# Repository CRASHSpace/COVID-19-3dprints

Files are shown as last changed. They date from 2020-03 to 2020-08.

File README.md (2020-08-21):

# COVID-19 3D prints and projects

I. [About us / Our work](#our-work)

II. [Designs](#print-or-laser-cut-ear-savers)

III. [Current needs / print recommendations](#print-recommendation) - Updated 8/21

IV. [Getting parts to us](#drop-off)

*This repo will stay updated with the latest information and source files.*

## Our work

CRASH Space has been working with USC Keck, Cedars-Sinai and others on the front line of this pandemic. With these clinical partners, we have developed and refined designs for face shields, face masks and ear savers, and rallied the community to build them. For the latest information on our work: [https://covid.crashspace.org](https://covid.crashspace.org)

We launched [our GoFundMe](https://charity.gofundme.com/o/en/campaign/makers-united-against-covid-19) on 4/10, and cannot thank our donors enough.

If you'd like to help build or assemble, let us know at covid@crashspace.org or on [this volunteer form](https://docs.google.com/forms/d/e/1FAIpQLSczant_0pGT0tIEJhOTPQsQpFoTAtQAkubEGK8ArdoSDPgAVQ/viewform).

### Drop off
We are collecting donations and assembling kits at: 6323 W 80th St, Los Angeles, CA 90045. Times will be posted on [our calendar](https://calendar.google.com/calendar/embed?src=crashspacela@gmail.com&ctz=America/Los_Angeles).

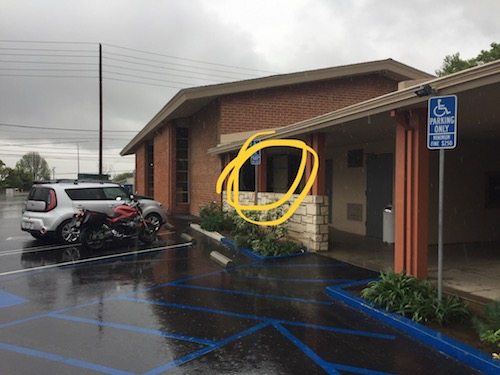
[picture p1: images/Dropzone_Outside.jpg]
Dropzone outside


No contact drop-off area:

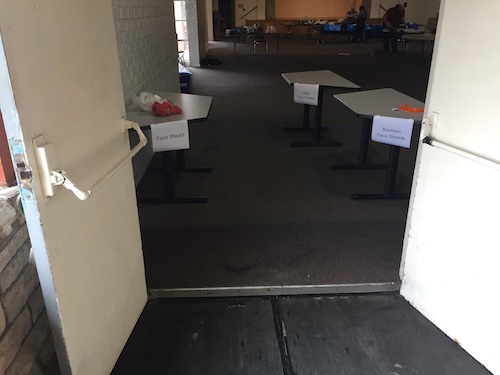
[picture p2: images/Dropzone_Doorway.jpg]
Dropzone doorway drop


**IF YOU MAKE SOMETHING**, please let us know here (We love pictures!): [https://airtable.com/shrZCoERKFkLPPHIm](https://airtable.com/shrZCoERKFkLPPHIm)

**IF YOU'D LIKE A DONATION RECEIPT**, you can get one here: [https://airtable.com/shrjphZT0ER9aLhNy](https://airtable.com/shrjphZT0ER9aLhNy)

## Print recommendation:

**As of late July**, demand for clinical face shields has tapered off as supply chains have caught up. We will announce periodic sprint runs as individual requests come in, and maintain this page for others wanting to produce PPE designs we've validated. As the situation evolves, we too will adapt.

[Sprint Run 8/14 - 8/26: 3DVerkstan Face Shields, V5](#sprint-run-814---826-3dverkstan-face-shields-v5) -- Extended to 8/26

[Sanitation Guidelines](https://github.com/CRASHSpace/COVID-19-3dprints/tree/master/Sanitation%20Guidelines_20200329.pdf)

---

## Sprint Run 8/14 - 8/26: 3DVerkstan Face Shields, V5
[https://github.com/CRASHSpace/COVID-19-3dprints/tree/master/Face%20Shield/3DVerkstan](https://github.com/CRASHSpace/COVID-19-3dprints/tree/master/Face%20Shield/3DVerkstan)

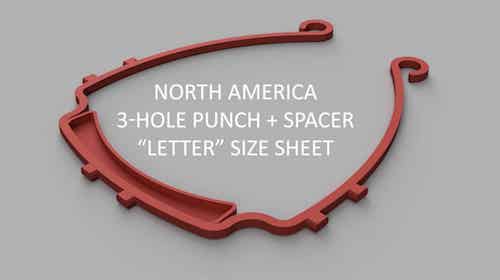
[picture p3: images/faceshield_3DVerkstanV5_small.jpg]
Face shield


LA EOC requested 2000 non-clinical face shields. We can handle making the shields, but need visors printed.

*If you are making some for yourself or another group and need the shield information*: This version uses clear 8.5" x 11" sheets, [3-hole punched to this shape](https://github.com/CRASHSpace/COVID-19-3dprints/raw/master/Face%20Shield/3DVerkstan/Verkstan-3HolePunch-CRASHSpaceMod.pdf). Instructions [here](https://www.youtube.com/watch?v=rz36MhT7p-c&feature=youtu.be). **OR** for large numbers, make [this drill jig from Midsouth Makers](http://www.midsouthmakers.org/2020/04/memphis-fighting-covid-transparency-drilling-rig/#MemphisFightingCOVID)
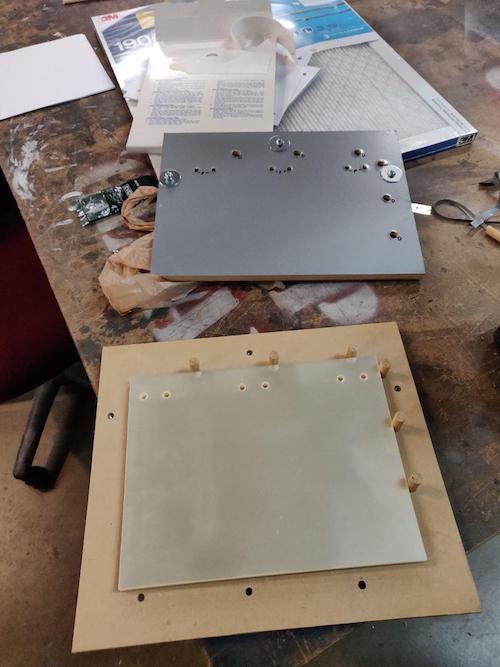
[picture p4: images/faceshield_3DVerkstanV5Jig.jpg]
Verkstan drill jig


## Budmen Face Shields V5 
[https://github.com/CRASHSpace/COVID-19-3dprints/tree/master/Face%20Shield/Budmen%20Face%20Shield/V5](https://github.com/CRASHSpace/COVID-19-3dprints/tree/master/Face%20Shield/Budmen%20Face%20Shield/V5)

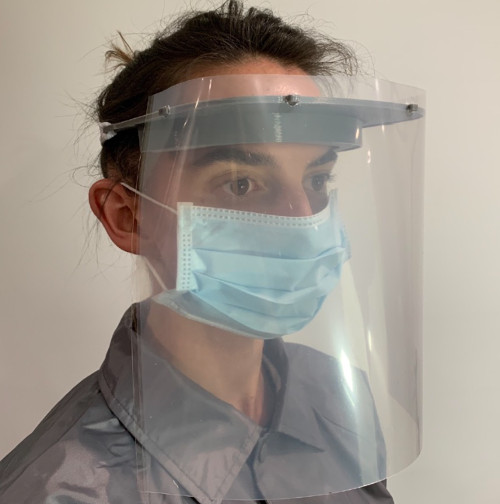
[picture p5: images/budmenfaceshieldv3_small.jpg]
Face shield


Cedars and Keck approved for immediate use. Assembly instructions are [here](https://youtu.be/I1LvKaha7R0). As of 5/25, we are receiving injection molded visors to fill our outstanding requests.

**NOTE:** Our template is different from the stock Budmen shield: [Modified Cedars Budmen shield template](https://github.com/CRASHSpace/COVID-19-3dprints/raw/master/Face%20Shield/Budmen%20Face%20Shield/V3/polysheet-templates/Cedars_Budmen_shield_v1.pdf). Laser template is here: [Cedars_Budmen_shield_v1cut.pdf](https://github.com/CRASHSpace/COVID-19-3dprints/raw/master/Face%20Shield/Budmen%20Face%20Shield/V3/polysheet-templates/Cedars_Budmen_shield_v1cut.pdf)

## Budmen Scrunchie strap
[https://github.com/CRASHSpace/COVID-19-3dprints/tree/master/Face%20Shield/CRASHSpace%20Scrunchy%20Headband](https://github.com/CRASHSpace/COVID-19-3dprints/tree/master/Face%20Shield/CRASHSpace%20Scrunchy%20Headband)

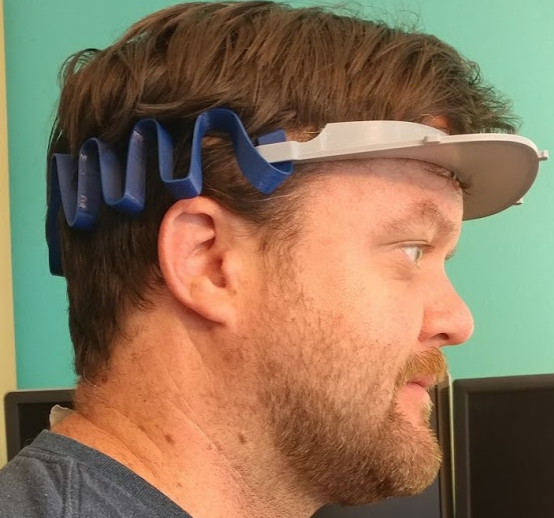
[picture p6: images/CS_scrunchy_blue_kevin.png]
Budmen Scrunchie Strap


Made in response to elastic shortages we faced one month in, these are also more easily sanitized than elastic. Very useful for remote hospitals. PET or PETG only.

## Ear Savers
[https://github.com/CRASHSpace/COVID-19-3dprints/tree/master/Ear%20Savers](https://github.com/CRASHSpace/COVID-19-3dprints/tree/master/Ear%20Savers)

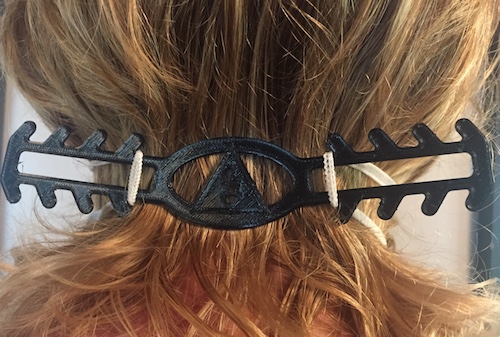
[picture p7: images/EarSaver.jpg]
Ear Saver


Mask bands not tugging on ears == More comfortable. More comfortable == Wear the mask longer (**safer**) + Adjust the mask less (**safer**). If you have a smaller printer, making these is a perfect way to help.

## Fabric Face Masks
[https://github.com/CRASHSpace/COVID-19-3dprints/tree/master/Sewn%20Face%20Mask/COVID_SewnMask-Instructions_v9.pdf](https://github.com/CRASHSpace/COVID-19-3dprints/tree/master/Sewn%20Face%20Mask/COVID_SewnMask-Instructions_v9.pdf)

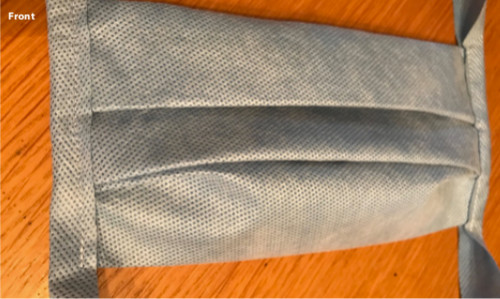
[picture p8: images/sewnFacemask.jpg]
Sewn Face Mask


## USCSW Face Masks
[https://github.com/CRASHSpace/COVID-19-3dprints/tree/master/Face%20Mask](https://github.com/CRASHSpace/COVID-19-3dprints/tree/master/Face%20Mask)

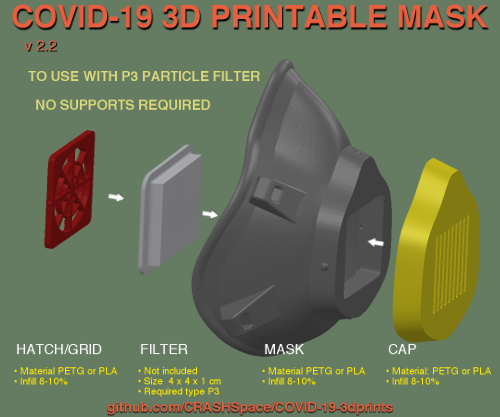
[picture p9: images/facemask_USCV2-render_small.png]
Face Mask Assembly


As of 5/25, we have filled our outstanding requests. We can collect any you have already printed.

## Laser Cut Aerosol Box
[https://github.com/CRASHSpace/COVID-19-3dprints/raw/master/Cedars%20Aerosol%20Box](https://github.com/CRASHSpace/COVID-19-3dprints/raw/master/Cedars%20Aerosol%20Box)

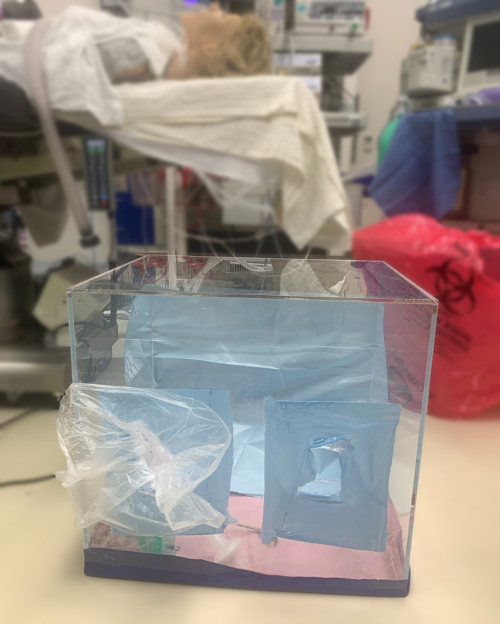
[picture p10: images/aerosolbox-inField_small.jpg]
Cedars Aerosol Box


**Delivered:** 1 evaluation unit for intubation testing

## SMP Face Shield
Just informational. **USC Keck evaluated**, and chose the Budmen design instead.

[https://github.com/CRASHSpace/COVID-19-3dprints/tree/master/Face%20Shield/SMP%20Face%20Shield](https://github.com/CRASHSpace/COVID-19-3dprints/tree/master/Face%20Shield/SMP%20Face%20Shield)

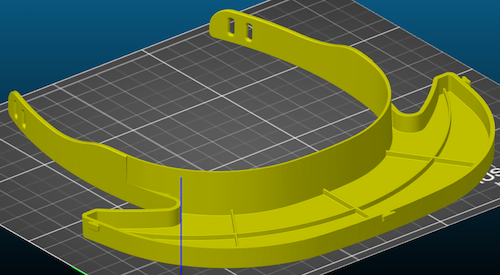
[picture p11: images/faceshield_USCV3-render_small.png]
SMP Face shield


# THANK YOU. Yes, you.

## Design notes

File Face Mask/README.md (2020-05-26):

# Face Masks (USC Keck modified Lowell design)—V3a updated 5/13
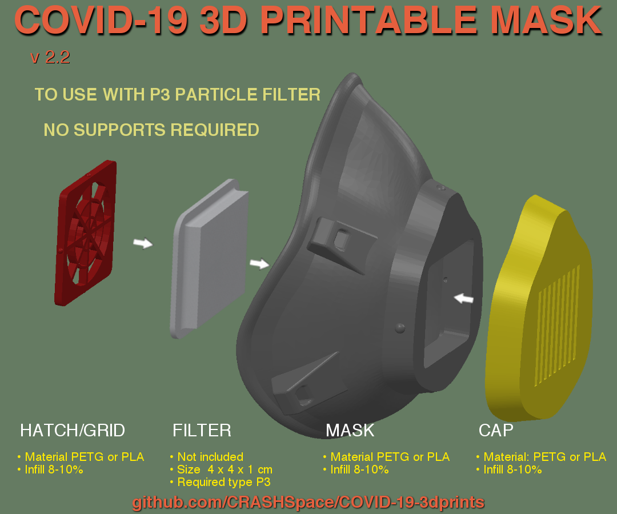
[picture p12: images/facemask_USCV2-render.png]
Face mask render


## Each mask consists of:
**1 x** [USCSW-Filtered_Mask-v3L.stl](https://github.com/CRASHSpace/COVID-19-3dprints/raw/master/Face%20Mask/USCSW-Filtered_Mask-v3L.stl) **OR**

[USCSW-Filtered_Mask-v3M.stl](https://github.com/CRASHSpace/COVID-19-3dprints/raw/master/Face%20Mask/USCSW-Filtered_Mask-v3M.stl) **OR**

[USCSW-Filtered_Mask-v3S.stl](https://github.com/CRASHSpace/COVID-19-3dprints/raw/master/Face%20Mask/USCSW-Filtered_Mask-v3S.stl),

**1 x** [USCSW_Nose_Cap_v3.stl](https://github.com/CRASHSpace/COVID-19-3dprints/raw/master/Face%20Mask/USCSW_Nose_Cap_v3.stl)

*and*

**1 x** [USCSW_Hatch_v2r1.stl](https://github.com/CRASHSpace/COVID-19-3dprints/raw/master/Face%20Mask/USCSW_Hatch_v2r1.stl)

*Above files are from USC Keck* [here](https://drive.google.com/drive/folders/11wPkq75T5fu1r9JX5doEOuPz13cvkt-k). GitHub copies here are intended as backup.

USCSW_gasket_x5S.stl, USCSW_gasket_x5M.stl and USCSW_gasket_x5L.stl are for molding tests. DON'T PRINT

**Print material:** PETG or PLA

**Suggested settings:** *Largest layer size option, up to 0.6mm DRAFT* with *~10% infill*.

## Parts you need to assemble:
DO NOT assemble if delivering to USC Keck. This is for assembling one for yourself.

* [Frost King 5/16" x1/4" D Profile Premium Rubber Self-Stick Weatherseal](https://smile.amazon.com/Frost-King-Self-Stick-Weatherseal-D-Section/dp/B000B4N3O0/ref=sr_1_1?keywords=Frost+King+5%2F16%22+x1%2F4%22+D+Profile+Premium+Rubber+Self-Stick+Weatherseal&qid=1585453260&s=home-garden&sr=1-1). 
* [Honeywell HEPA filter model HRF201B](https://smile.amazon.com/Flintar-Replacement-Compatible-Honeywell-HRF201B/dp/B07SQ5NHJ7/ref=sr_1_5)
* 1/4" or 1/2" Elastic

**[Assembly Guidelines](https://github.com/CRASHSpace/COVID-19-3dprints/blob/master/Face%20Mask/Pseudo%20N95%203D%20Printed%20Masks.pdf)**  

**[Assembly Video - Youtube](https://www.youtube.com/watch?v=TImIaytAqlc&feature=youtu.be)**

## Did you print one?
They would also like to know the following:

Name/Company (opt.)

Date

Qty

Printer type

Print materials

This can be recorded [here](https://airtable.com/shrZCoERKFkLPPHIm), or written and submitted with prints.

### 3/29 Update:
> Heads up. I received a batch with some print issues. Some surface imperfections is fine, but issues with the filter interface is bad. Please check to see if those print areas are free of issues before dropping off. That would be awesome.
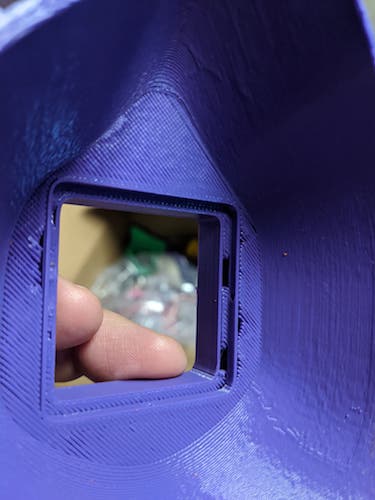
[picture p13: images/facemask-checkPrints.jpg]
Check Prints


### Information:
> We are accepting 3D printed parts. Keck Medical Center will finish attaching padding, filter, and elastic straps. We have two sizes of mask. Currently we are looking to produce a 2:1  M:L. If you are making these for other place or for personal use, we are using [Frost King 5/16" x1/4" D Profile Premium Rubber Self-Stick Weatherseal](https://smile.amazon.com/Frost-King-Self-Stick-Weatherseal-D-Section/dp/B000B4N3O0/ref=sr_1_1?keywords=Frost+King+5%2F16%22+x1%2F4%22+D+Profile+Premium+Rubber+Self-Stick+Weatherseal&qid=1585453260&s=home-garden&sr=1-1). We are sealing around the outer edge with hot glue, but we are experimenting the Flex Seal. The filter is a Honeywell [HEPA filter model HRF201B](https://smile.amazon.com/Flintar-Replacement-Compatible-Honeywell-HRF201B/dp/B07SQ5NHJ7/ref=sr_1_5).
> 
> We are currently printing a variant of the pseudo N95 mask found on [https://lowellmakes.com/covid-19-response/](https://lowellmakes.com/covid-19-response/)
> 
> I’ve included our variants of their model. We are working on more thing including different sizes as well as a process to cast them using resin. I will update people as new models come out.
> 
> We are also working with people to produce face shields. Many of the designs out in the world right now are not wide enough for the liking of our Infection Prevention team. We are laser cutting 13 “ x 9.5” shields and 3D printing head bands. That design is also included (please note the attachment points on the model may need scaling for the thickness of the shield material).
> Any assistance would be most welcomed.
> 
> **Darryl H. Hwang, PhD**
> 
> Assistant Professor of Research, Department of Radiology, Keck School of Medicine
> Assistant Professor of Research, Department of Biomedical Engineering, Viterbi School of Engineering
> Director, 4D Quantitative Imaging Lab, Keck Medical Center of USC

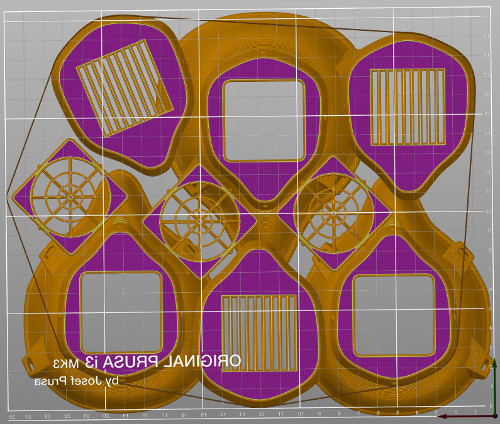
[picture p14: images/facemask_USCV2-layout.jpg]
Face mask layout


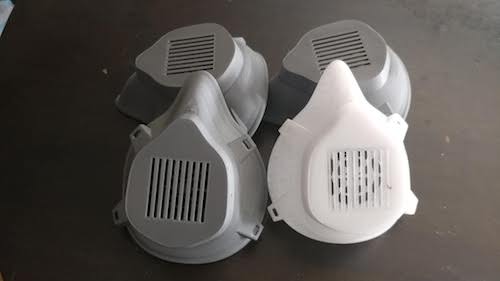
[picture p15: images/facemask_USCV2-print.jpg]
Assembled Face masks


### Source:
Files are **MODIFIED** versions of [Lowell design](https://lowellmakes.com/covid-19-response/)

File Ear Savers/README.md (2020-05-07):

# Ear Savers
Ear Saver

## One part print:
**1 x** [CS CutOut Ear Saver.stl](https://github.com/CRASHSpace/COVID-19-3dprints/raw/master/Ear%20Savers/CS%20CutOut%20Ear%20Saver.stl)

**Print material:** PETG or PLA

## Or Laser Cut:
**Full sheets** 

[EarSaversFullsheet_CS_v2.pdf](https://github.com/CRASHSpace/COVID-19-3dprints/raw/master/Ear%20Savers/EarSaversFullsheet_CS_v2.pdf)

[EarSaversFullsheet_CS_v2.ai](https://github.com/CRASHSpace/COVID-19-3dprints/raw/master/Ear%20Savers/EarSaversFullsheet_CS_v2.ai)

**1 x** [EarSaversSingle_CS.ai](https://github.com/CRASHSpace/COVID-19-3dprints/raw/master/Ear%20Savers/EarSaversSingle_CS.ai)

## Did you print one?
They would also like to know the following:

|||
|--- |--- |
|Name/Company| _(optional)_|
|Date| |
|Quantity| |
|Printer type| |
|Print materials| |

This can be recorded [here](https://airtable.com/shrZCoERKFkLPPHIm), or written and submitted with prints.

### Information on Request:
Multiple hospitals have requested these. It makes wearing a mask all day far more comfortable, since the elastic tugs on these instead of your ears.

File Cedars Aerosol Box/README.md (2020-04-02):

# Aerosol box
Intended use:

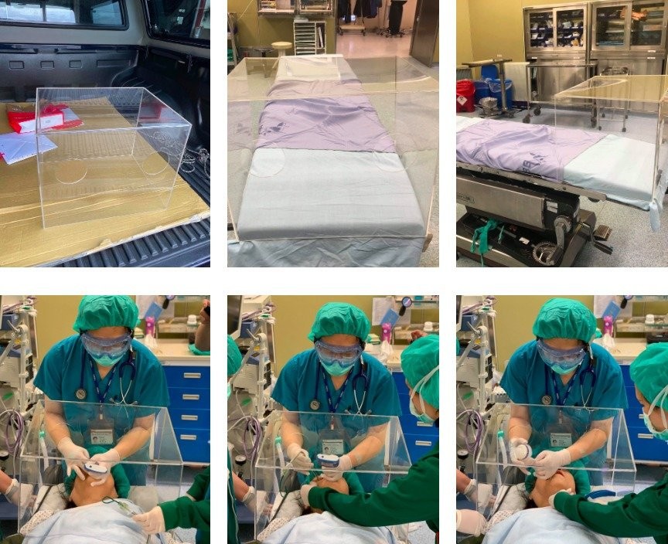
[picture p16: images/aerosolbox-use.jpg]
Intubating patient


## Each unit consists of:
**5 x** Acrylic parts to be cut and plastic welded according to [Aerosol Box.pdf](https://github.com/CRASHSpace/COVID-19-3dprints/raw/master/Cedars%20Aerosol%20Box/Aerosol%20Box.pdf)

## Information on Request:
We delivered a unit to Cedars-Sinai, who requested a unit to evaluate its effectiveness in protecting staff while intubating a patient.

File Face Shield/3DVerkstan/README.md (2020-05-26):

# 3DVerkstan V5 Face Shields
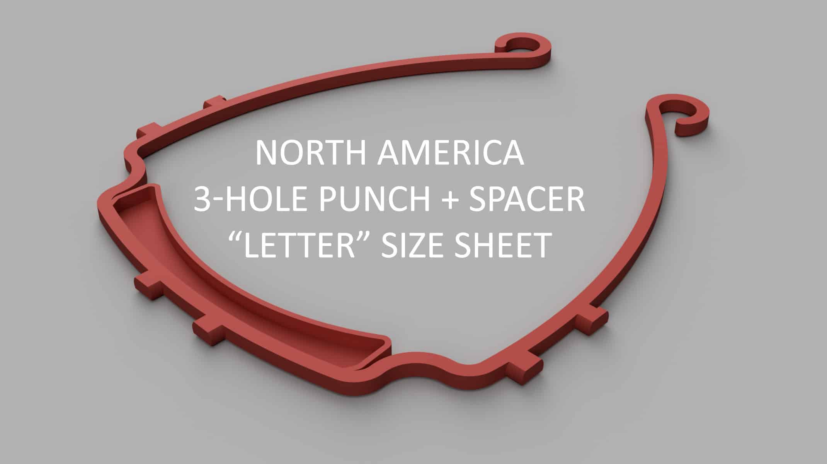
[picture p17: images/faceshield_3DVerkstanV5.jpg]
3DVerkstan Face shield


## Each mask consists of:
**1 x** [Visor_Frame_NORTH_AMERICA_letter_6-hole_v5.stl](https://github.com/CRASHSpace/COVID-19-3dprints/raw/master/Face%20Shield/3DVerkstan/Visor_Frame_NORTH_AMERICA_letter_6-hole_v5.stl)

**1 x** 0.005in thick poly sheet 3-hole punched to guides in [Verkstan-3HolePunch-CRASHSpaceMod.pdf](https://github.com/CRASHSpace/COVID-19-3dprints/raw/master/Face%20Shield/3DVerkstan/Verkstan-3HolePunch-CRASHSpaceMod.pdf)

*and*

**(optional) 1 x** Rubber band

**Print material:** PETG or PLA

**Suggested settings:** *Largest layer size option, up to 0.8mm DRAFT* with *~10% infill*.

### 3DVerkstan Instructions on how to do the punching:

[Video How To](https://www.youtube.com/watch?v=rz36MhT7p-c&feature=youtu.be)

1. Print out the [3 hole punch guide.](https://github.com/CRASHSpace/COVID-19-3dprints/raw/master/Face%20Shield/3DVerkstan/Verkstan-3HolePunch-CRASHSpaceMod.pdf) 100%

2. Tape the guide into your 3-hole punch aligning the first hole to align with the hole punch.

4. To make 12"x11" shields, put the 12" side towards the hole punch. Punch 3 holes

5. Slide the punched plastic sheet to the right, aligning with the guide, and punch 3 more holes.

## Did you print one?
They would also like to know the following:

Name/Company (opt.)

Date

Qty

Printer type

Print materials

This can be recorded [here](https://airtable.com/shrZCoERKFkLPPHIm), or written and submitted with prints.

### Information on Request:
These are being given to non-clinical users.

### Source:
3DVerkstan: [https://3dverkstan.se/protective-visor/protective-visor-versions/](https://3dverkstan.se/protective-visor/protective-visor-versions/)

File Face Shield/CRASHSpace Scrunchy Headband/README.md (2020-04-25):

# CRASHSpace Scrunchy Headband for Budmen Shield
Print!

This is a replacement for the elastic band on the Budmen design. This scrunchy snaps into place and tensions around the user's head to keep the mask firmly in place.

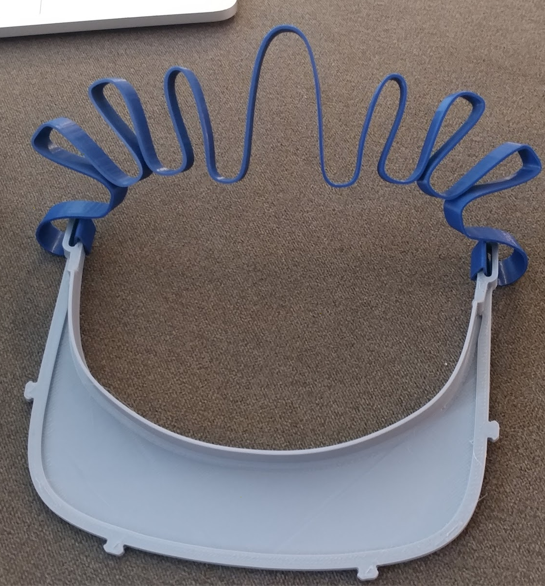
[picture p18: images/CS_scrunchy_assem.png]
CRASHSpace Scrunchy Headband


CRASHSpace Scrunchy Headband

The shortage of elastic is causing us to reconsider how to attach the shields to workers heads. This design requires no elastic and is faster to assemble than with elastic.

Suggest printing in PETG for flexibility.

[CRASHSpace Scrunchy Headband for Budmen Sheild - Large version - STL](https://github.com/CRASHSpace/COVID-19-3dprints/raw/master/Face%20Shield/CRASHSpace%20Scrunchy%20Headband/Crashspace_scrunchy-Budmen-Largev1.STL)

[CRASHSpace Scrunchy Headband for Budmen Sheild - Small version - STL](https://github.com/CRASHSpace/COVID-19-3dprints/raw/master/Face%20Shield/CRASHSpace%20Scrunchy%20Headband/Crashspace_scrunchy-Budmen-Smallv1.STL)

While printing, please set your seam to "Rear" or not on the path. 
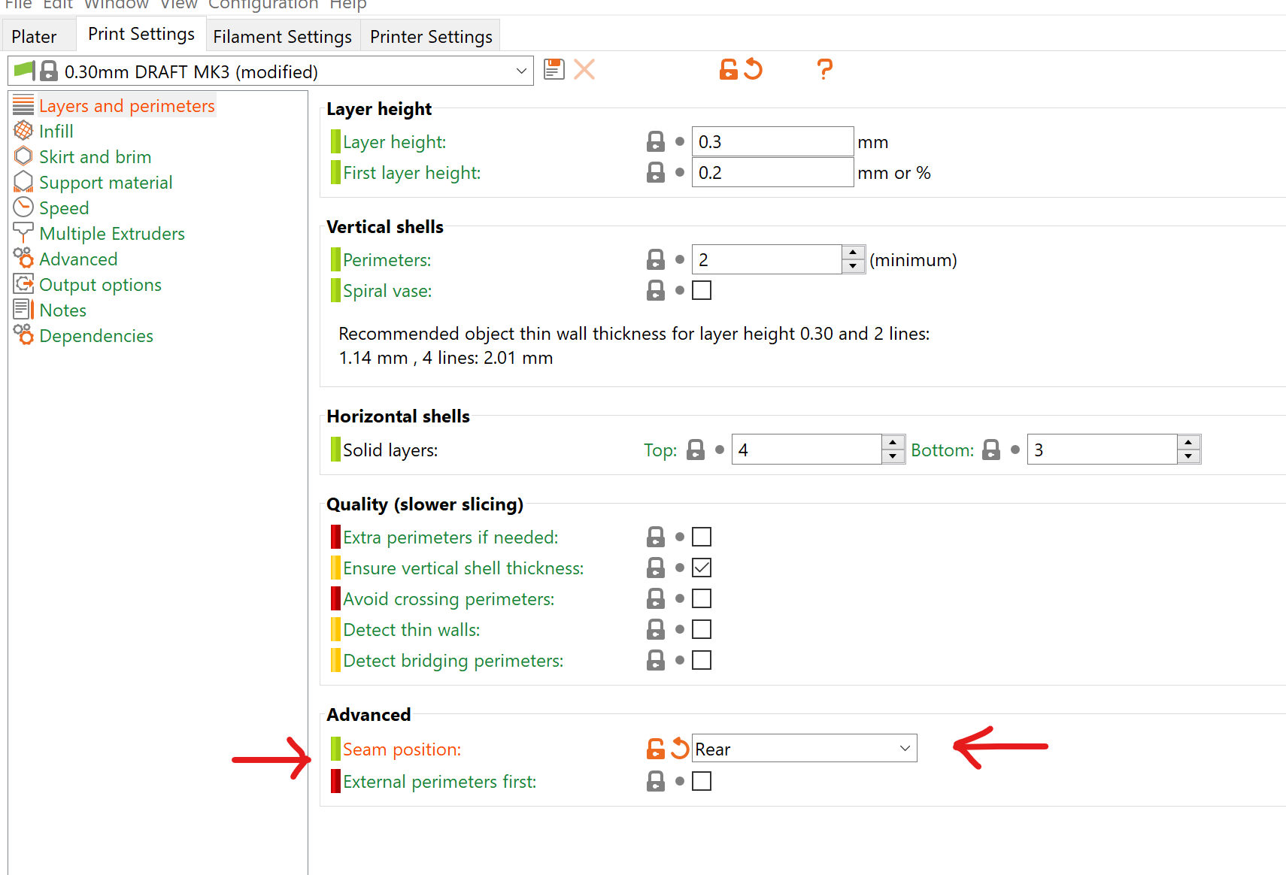
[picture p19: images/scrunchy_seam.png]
Rear Seam


Here is an example with what happens with another scrunchy type design:

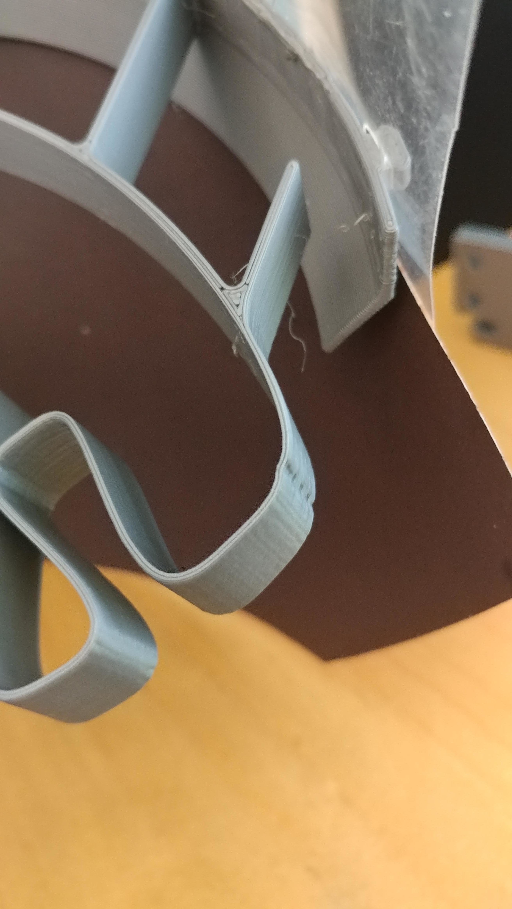
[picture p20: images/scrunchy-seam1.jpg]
Weak Seam


This design is based off the design of [FaceShield.us](https://FaceShield.us). Thanks Peter Vikar!

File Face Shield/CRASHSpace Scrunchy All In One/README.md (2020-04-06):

# CRASHSpace Scrunchy Face Shield
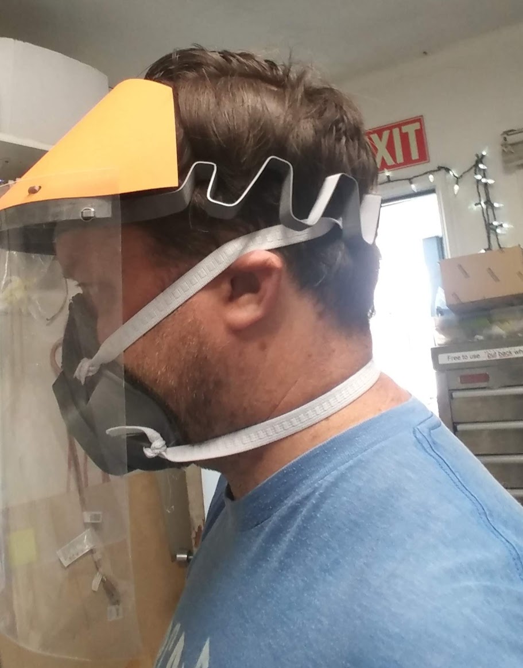
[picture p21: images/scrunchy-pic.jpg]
CRASHSpace Scrunchy Face Shield


This is a work in progress. Do not print yet.

If you do print, please set your seam to Rear
Rear Seam

or your print will have a weak point:

Weak Seam

This design is based off the design of [FaceShield.us](https://FaceShield.us). Modified to use have a head cover. No elastic needed. Also design help from Yotam Barr.

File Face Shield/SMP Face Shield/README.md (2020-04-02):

# Face Shields for USC Keck (Archived 4/1/2020)
USC Keck evaluated this design and its modifications, and after consideration, chose the Budmen design instead.

Face shield

## Each shield consists of:

**1 x** [SMP Face Shield rev3.stl](https://github.com/CRASHSpace/COVID-19-3dprints/raw/master/Face%20Shield/SMP%20Face%20Shield/SMP%20Face%20Shield%20rev3.stl)

*and* 

**1 x** polycarbonate sheet *cut to*: [Universal face shield.PDF](https://github.com/CRASHSpace/COVID-19-3dprints/raw/master/Face%20Shield/SMP%20Face%20Shield/Universal%20face%20shield.PDF)

**Print material:** *PETG* or *PLA*

**Suggested settings:** *0.3mm DRAFT* (if available, otherwise largest layer size) with *~10% infill* and *support on base layer only*

**Prusa pre-laid 3MF:** [SMP Face Shield rev3_SUPPORT.3mf](https://github.com/CRASHSpace/COVID-19-3dprints/raw/master/Face%20Shield/SMP%20Face%20Shield/SMP%20Face%20Shield%20rev3_SUPPORT.3mf)

### Source:
File is a **MODIFIED** version of Budmen: [https://budmen.com/](https://budmen.com/)

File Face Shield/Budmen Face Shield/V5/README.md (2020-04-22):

# Budmen V5 Face Shields for Cedars-Sinai and USC Keck

## Each mask consists of:
**1 x** [3D-files/face-shield.stl](https://github.com/CRASHSpace/COVID-19-3dprints/raw/master/Face%20Shield/Budmen%20Face%20Shield/V5/3D-files/USCBM_Faceshield-V5.stl)

**2 x** [3D-files/20mm_strap_lock.stl](https://github.com/CRASHSpace/COVID-19-3dprints/raw/master/Face%20Shield/Budmen%20Face%20Shield/V5/3D-files/20mm_strap_lock.stl) ( We are not using the [1/4" strap lock](3D-files/strap-lock.stl) at this time)

**1 x** 0.005in thick poly sheet cut to template: [polysheet-templates/Cedars_Budmen_shield_v1.pdf](https://github.com/CRASHSpace/COVID-19-3dprints/raw/master/Face%20Shield/Budmen%20Face%20Shield/V5/polysheet-templates/Cedars_Budmen_shield_v1.pdf) 

Laser template: [polysheet-templates/Budmen_Cedars_shield_v1cut.pdf](https://github.com/CRASHSpace/COVID-19-3dprints/raw/master/Face%20Shield/Budmen%20Face%20Shield/V5/polysheet-templates/Cedars_Budmen_shield_v1cut.pdf)

*and*

**1 x** Foam Tape 3/4in x 1/2in thick, cut 9.5in long

**Print material:** PETG or PLA

**Suggested settings:** *0.3mm DRAFT* with *~10% infill*, *4 solid top layers* and *3 solid bottom layers*.

**Prusa pre-laid 3MF:** [3D-files/BudmenV3_2face_shields-Pre-laid-out.3mf](https://github.com/CRASHSpace/COVID-19-3dprints/raw/master/Face%20Shield/Budmen%20Face%20Shield/V5/3D-files/BudmenV5_2face_shields-Pre-laid-out.3mf)

## Did you print one?
They would also like to know the following:

|||
|--- |--- |
|Name/Company| _(optional)_|
|Date| |
|Quantity| |
|Printer type| |
|Print materials| |

This can be recorded [here](https://airtable.com/shrZCoERKFkLPPHIm), or written and submitted with prints.

### Information on Request:
Cedars-Sinai evaluated and approved this design, as did USC Keck. They evaluated V4 and **disapproved** due to the shield clips preventing larger shields from being used.

### Source:
This is a **modified** version of the Budmen design, allowing for larger shields (cutout patterns are not interchangable): [https://budmen.com/](https://budmen.com/)

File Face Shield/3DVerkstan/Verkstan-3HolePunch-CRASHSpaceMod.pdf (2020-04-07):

1) Align this line with hole in 3 hole punch Punch holes in clear plastic

to 3 hole punch

Tape this side

2) Shift plastic, align previous punched holes with this line Punch 2nd set of holes

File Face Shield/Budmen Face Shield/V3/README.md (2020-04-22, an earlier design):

### Budmen V3 Face Shields for Cedars-Sinai and USC Keck

# DEPRECATED. Print V5 instead [https://github.com/CRASHSpace/COVID-19-3dprints/tree/master/Face%20Shield/Budmen%20Face%20Shield/V5](https://github.com/CRASHSpace/COVID-19-3dprints/tree/master/Face%20Shield/Budmen%20Face%20Shield/V5)

---

<del>
## Each mask consists of:
**1 x** [3D-files/face-shield.stl](https://github.com/CRASHSpace/COVID-19-3dprints/raw/master/Face%20Shield/Budmen%20Face%20Shield/V3/3D-files/face-shield.stl)

**1 x** [3D-files/strap-lock.stl](https://github.com/CRASHSpace/COVID-19-3dprints/raw/master/Face%20Shield/Budmen%20Face%20Shield/V3/3D-files/strap-lock.stl)

**1 x** 0.005in thick poly sheet cut to template: [polysheet-templates/Budmen_Cedars_shield_v1.pdf](https://github.com/CRASHSpace/COVID-19-3dprints/raw/master/Face%20Shield/Budmen%20Face%20Shield/V3/polysheet-templates/Budmen_Cedars_shield_v1.pdf) 

Laser template: [polysheet-templates/Budmen_Cedars_shield_v1cut.pdf](https://github.com/CRASHSpace/COVID-19-3dprints/raw/master/Face%20Shield/Budmen%20Face%20Shield/V3/polysheet-templates/Budmen_Cedars_shield_v1cut.pdf)

*and*

**1 x** Foam Tape 3/4in x 1/2in thick, cut 9.5in long

**Print material:** PETG or PLA

**Suggested settings:** *0.3mm DRAFT* with *~10% infill*, *4 solid top layers* and *3 solid bottom layers*.

**Prusa pre-laid 3MF:** [3D-files/BudmenV3_2face_shields-Pre-laid-out.3mf](https://github.com/CRASHSpace/COVID-19-3dprints/raw/master/Face%20Shield/Budmen%20Face%20Shield/V3/3D-files/BudmenV3_2face_shields-Pre-laid-out.3mf)

### Information on Request:
Cedars-Sinai evaluated and approved this design, as did USC Keck. They evaluated V4 and **disapproved** due to the shield clips preventing larger shields from being used.

### Source:
Budmen: [https://budmen.com/](https://budmen.com/)
</del>

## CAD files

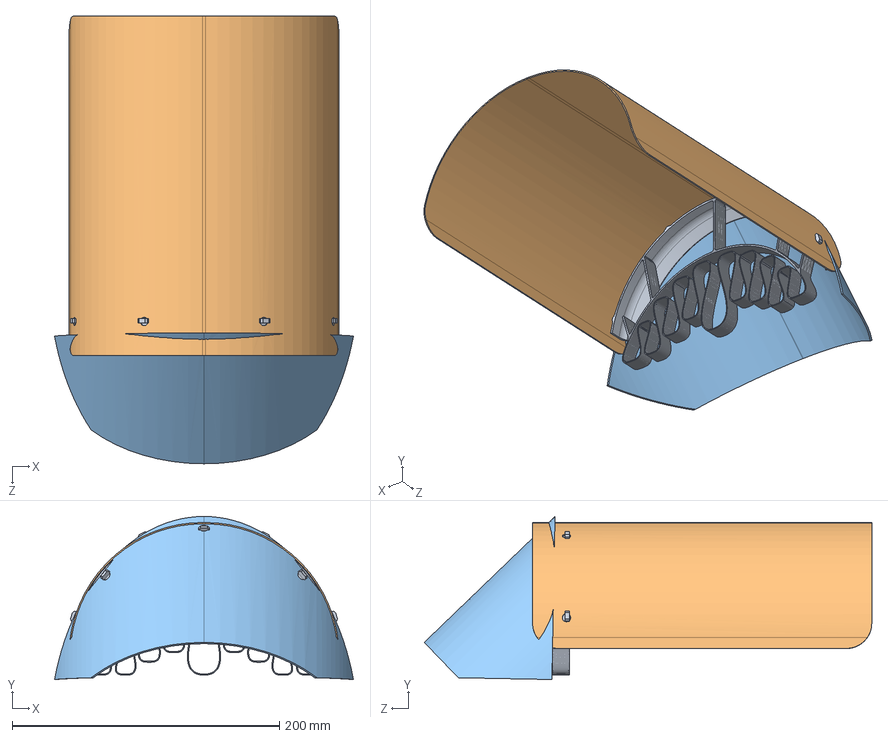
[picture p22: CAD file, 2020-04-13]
Face Shield/CRASHSpace Scrunchy Headband/Solidworks Files/Crashspace Scrunchy v1 Assem.SLDASM
223.9 x 122.1 x 335.2 mm
CrashspaceScrunchy v1
blast shield v1
Head Cover cylinder

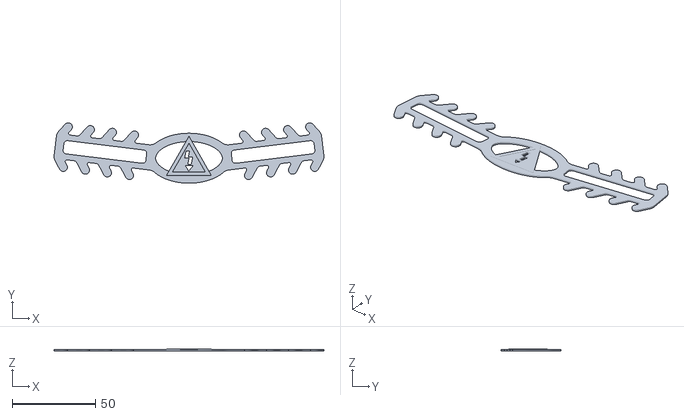
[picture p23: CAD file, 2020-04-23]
Ear Savers/CS CutOut Ear Saver.stl
161.9 x 36.3 x 1.25

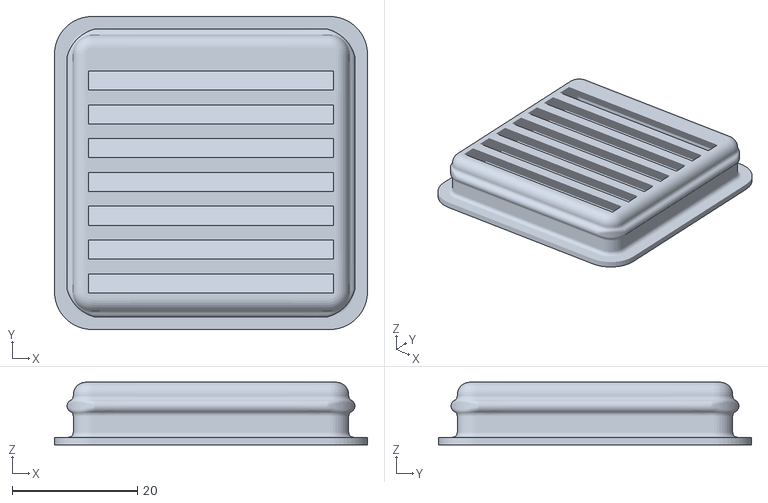
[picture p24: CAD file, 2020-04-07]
Face Mask/Evaluation/California/Filter Frame Slotted Snap.stl
50.0 x 50.0 x 10.0

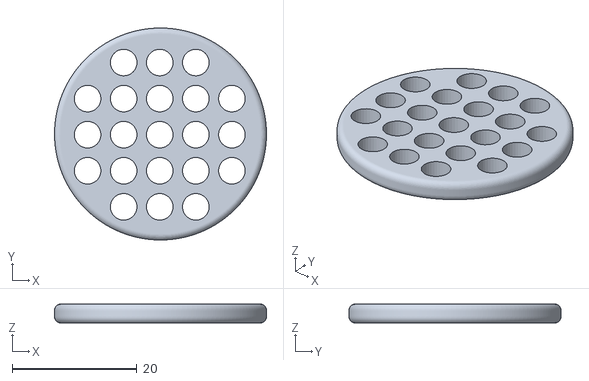
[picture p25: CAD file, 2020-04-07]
Face Mask/Evaluation/LaFactoriaV2/files/Filter_N95_holder.stl
34.0 x 34.0 x 3.00

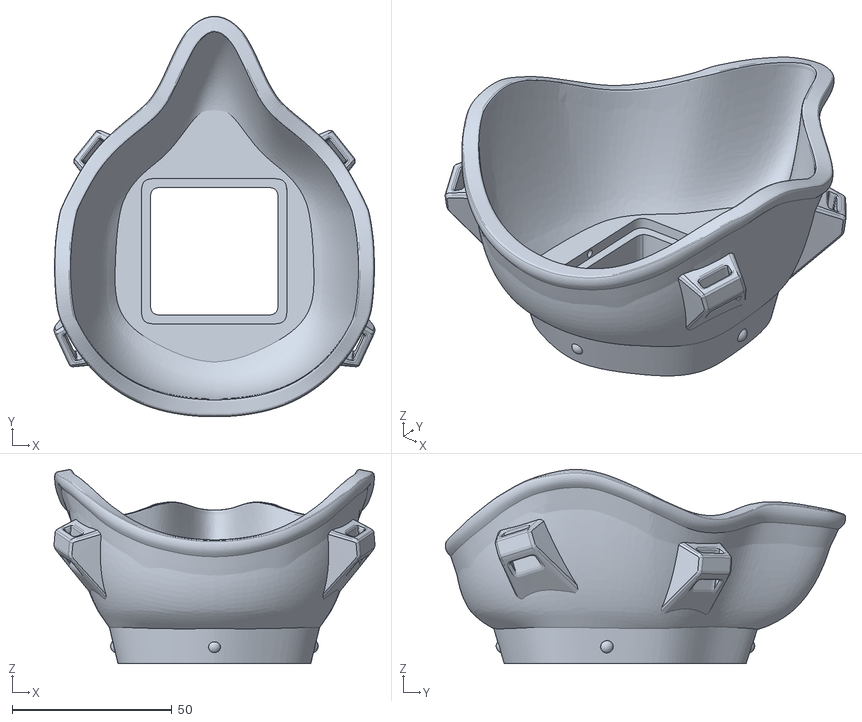
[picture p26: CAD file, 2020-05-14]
Face Mask/USCSW-Filtered_Mask-v3M.stl
100.4 x 125.2 x 60.7

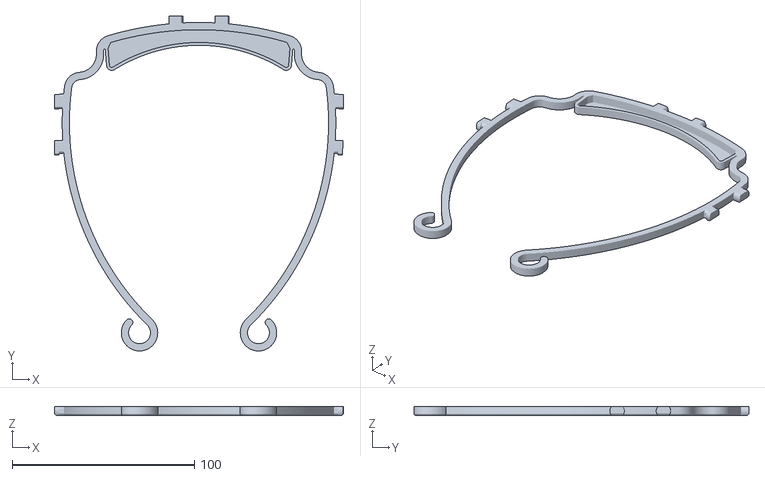
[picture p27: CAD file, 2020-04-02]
Face Shield/3DVerkstan/Visor_Frame_NORTH_AMERICA_letter_6-hole_v5.stl
158.5 x 183.6 x 5.00

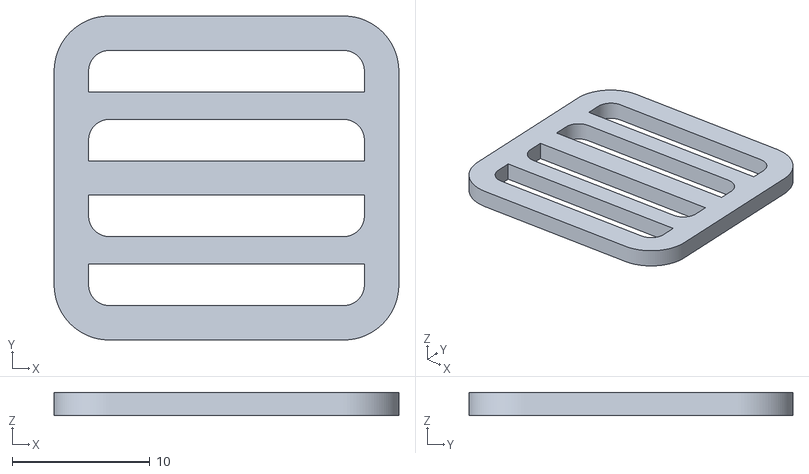
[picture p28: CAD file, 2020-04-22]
Face Shield/Budmen Face Shield/V5/3D-files/20mm_strap_lock.stl
25.0 x 23.5 x 1.68

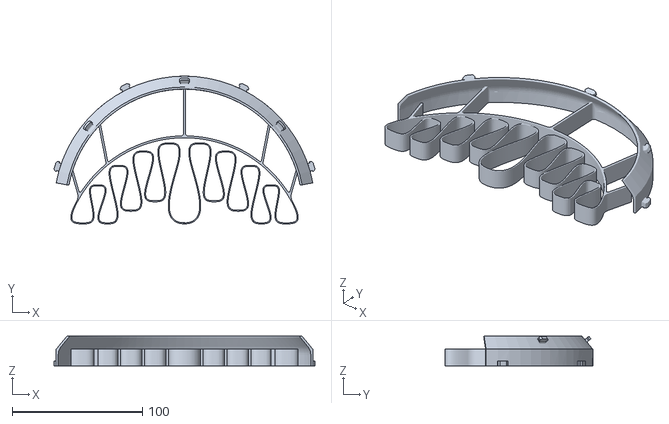
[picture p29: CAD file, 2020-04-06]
Face Shield/CRASHSpace Scrunchy All In One/CrashspaceScrunchy v1.STL
200.0 x 113.2 x 22.6

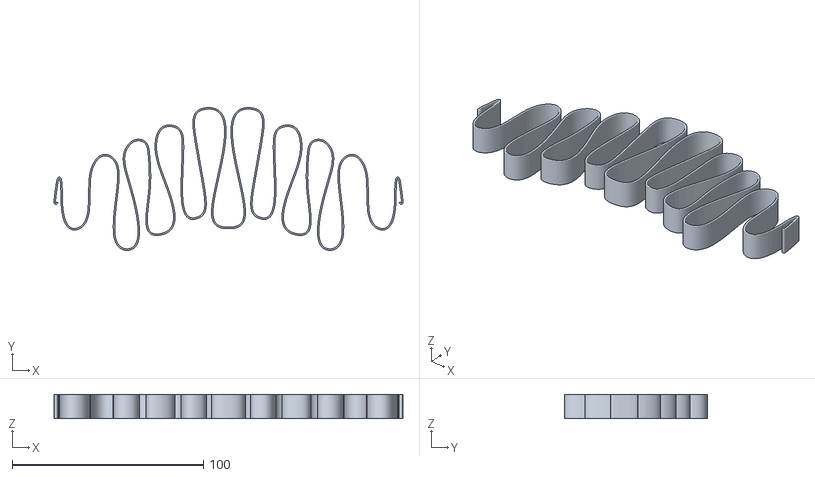
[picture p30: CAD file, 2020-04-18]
Face Shield/CRASHSpace Scrunchy Headband/Crashspace_scrunchy-Budmen-Largev1.STL
182.7 x 74.8 x 12.7

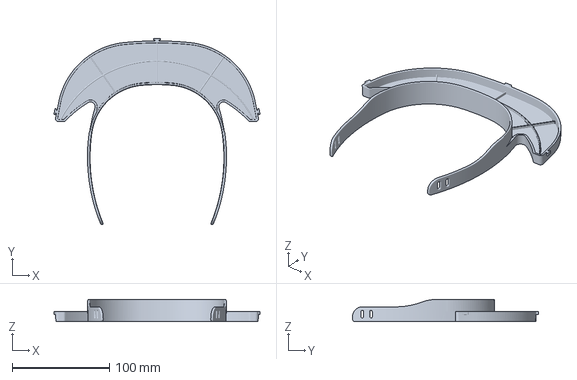
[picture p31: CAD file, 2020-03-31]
Face Shield/SMP Face Shield/SMP Face Shield rev3_SUPPORT.3mf
212.0 x 191.4 x 22.9 mm

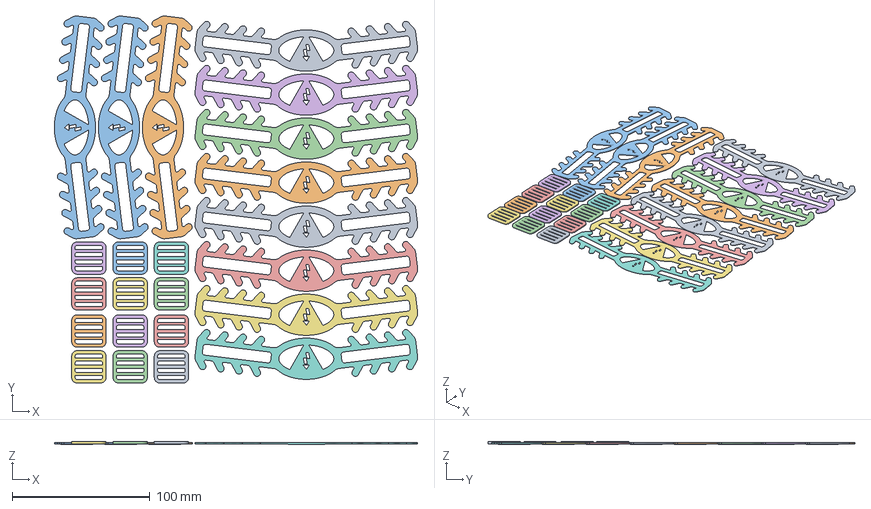
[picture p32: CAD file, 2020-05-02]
printfarm/MP10/0.4 Nozzle/PETG/Project Files/PETG_04_11XEarSaver_MP10.3mf
264.1 x 266.7 x 1.98 mm

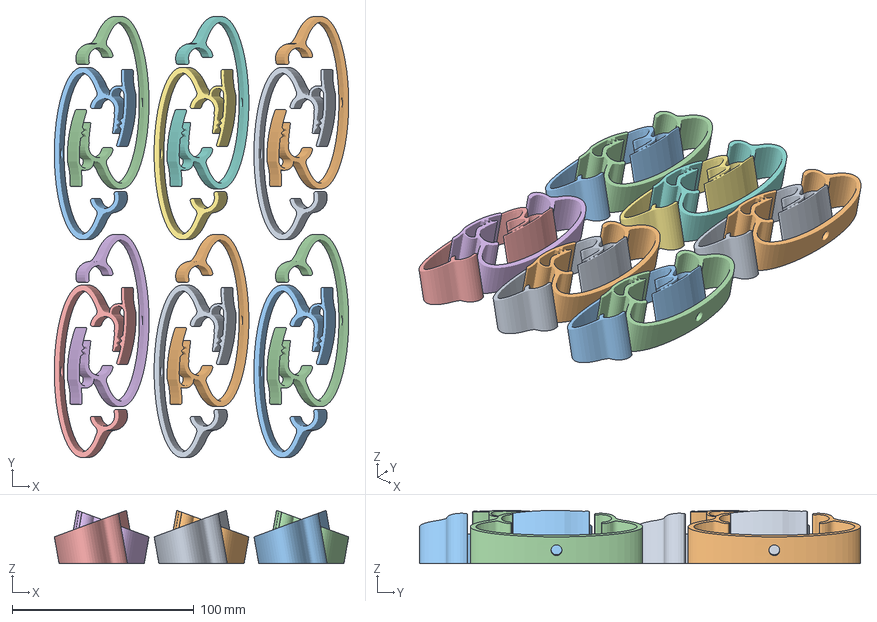
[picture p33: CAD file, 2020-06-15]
printfarm/MP10/0.4 Nozzle/PLA/Project Files/PLA_04_12X_CamClip_MP10.3mf
162.2 x 243.0 x 29.4 mm
Clip cam 7.8b_ThickerSpine2.stl
Clip cam 7.8b_ThickerSpine2.stl(1)
2X_ClipCam7.8b_ThickerSpine.3mf
2X_ClipCam7.8b_ThickerSpine.3mf(1)
2X_ClipCam7.8b_ThickerSpine.3mf(2)
2X_ClipCam7.8b_ThickerSpine.3mf(3)
2X_ClipCam7.8b_ThickerSpine.3mf(4)
2X_ClipCam7.8b_ThickerSpine.3mf(5)
2X_ClipCam7.8b_ThickerSpine.3mf(6)
2X_ClipCam7.8b_ThickerSpine.3mf(7)
2X_ClipCam7.8b_ThickerSpine.3mf(8)
2X_ClipCam7.8b_ThickerSpine.3mf(9)

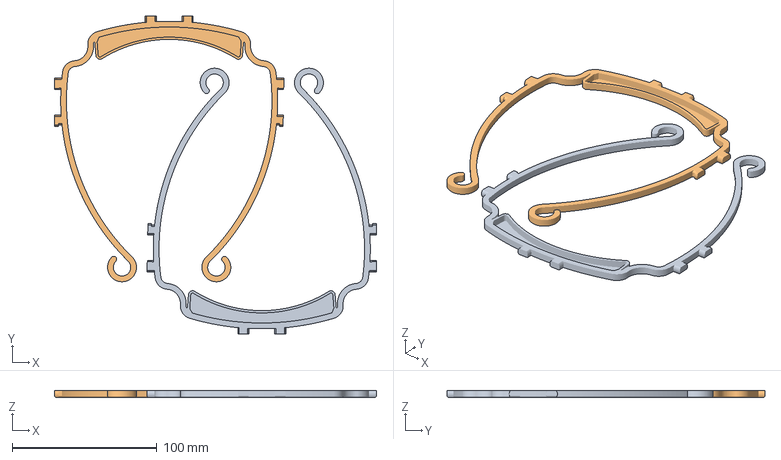
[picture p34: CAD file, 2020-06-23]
printfarm/MP10/0.6 Nozzle/PETG/Project Files/PETG_06_2X_Verkstan_MP10.3mf
222.5 x 219.6 x 5.00 mm
PLA_04_2X_Verkstan_MP10.3mf(1)
PLA_04_2X_Verkstan_MP10.3mf

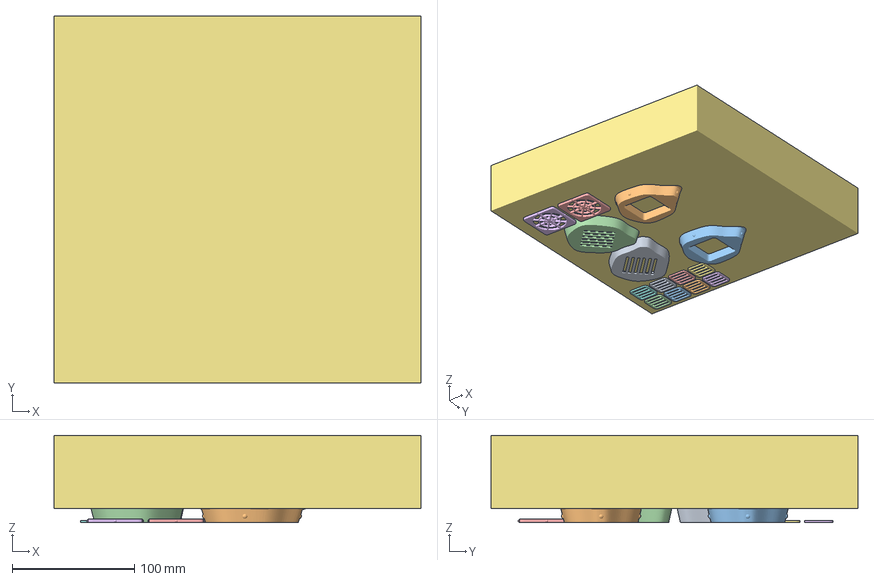
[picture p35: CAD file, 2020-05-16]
printfarm/MP10/0.6 Nozzle/PLA/Project Files/PLA_06_2X_mask-v3L_MP10.3mf
300.0 x 300.0 x 71.5 mm
PLA_06_2X_mask-v3L_MP10.3mf
PLA_06_2X_mask-v3L_MP10.3mf(1)
PLA_06_2X_mask-v3L_MP10.3mf(2)
PLA_06_2X_mask-v3L_MP10.3mf(3)
PLA_06_2X_mask-v3L_MP10.3mf(4)
PLA_06_2X_mask-v3L_MP10.3mf(5)
PLA_06_2X_mask-v3L_MP10.3mf(6)
PLA_06_2X_mask-v3L_MP10.3mf(7)
PLA_06_2X_mask-v3L_MP10.3mf(8)
PLA_06_2X_mask-v3L_MP10.3mf(9)
PLA_06_2X_mask-v3L_MP10.3mf(10)
PLA_06_2X_mask-v3L_MP10.3mf(11)
PLA_06_2X_mask-v3L_MP10.3mf(12)
PLA_06_2X_mask-v3L_MP10.3mf(13)
PLA_06_2X_mask-v3L_MP10.3mf(14)

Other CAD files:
Face Shield/CRASHSpace Scrunchy Headband/Solidworks Files/Crashspace_scrunchy-Budmen-Large.SLDPRT
printfarm/MP10/MP10_shieldV5_r041620_PLA.3mf
printfarm/MP10_Mini/0.4 Nozzle/PETG/Project Files/PETG_04_5XEarSaver_MP10mini.3mf
printfarm/MP10_Mini/0.4 Nozzle/PLA/Project Files/PLA_04_42X_straplock_mini.3mf
Face Mask/Evaluation/California/California Mask - Ridged.stl
Face Mask/Evaluation/California/California Mask.stl
Face Mask/Evaluation/LaFactoriaV2/files/Filter_N95_cap.stl
Face Mask/Evaluation/LaFactoriaV2/files/Filter_N95_connector.stl
Face Mask/Evaluation/LaFactoriaV2/files/Filter_connector_CUSTOMIZABLE.stl
Face Mask/Evaluation/LaFactoriaV2/files/Filter_standard_cap.stl
Face Mask/Evaluation/LaFactoriaV2/files/Filter_standard_connector.stl
Face Mask/Evaluation/LaFactoriaV2/files/Mask_body_L_thin.stl
Face Mask/Evaluation/LaFactoriaV2/files/Mask_body_L_wide.stl
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

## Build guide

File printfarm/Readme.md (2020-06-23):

# Crashspace Printfarm 

Crashspace received 10 Monoprice MP10 and 5 Monoprice MP10 Mini 3d printers from Monoprice. 

# GCode - Print files
Printer (Nozzle Diameter)

File         | MP10 (0.4mm)| MP10   (0.4mm)| MP10  (0.6mm)| MP10 (0.6mm)         |  MP10 Mini  (0.4mm)      |  MP10 Mini  (0.4mm)     | MP10 Mini  (0.6mm)   | MP10 Mini (0.6mm)     |
------------ | ---------- | -----------| -----------| ---------- | ------------- | ------------- | --------- | ---------   |
Filament Type| PETG       | PLA        | PETG       | PLA        | PETG          | PLA           | PETG      | PLA         | 
Budmen V5    | [4x Budmen PETG 0.4mm](https://github.com/CRASHSpace/COVID-19-3dprints/raw/master/printfarm/MP10/0.4%20Nozzle/PETG/PETG_04_4XshieldV5_MP10.gcode) | [4x Budmen PLA 0.4mm](https://github.com/CRASHSpace/COVID-19-3dprints/raw/master/printfarm/MP10/0.4%20Nozzle/PLA/PLA_04_100_4XshieldV5_MP10_r0421.gcode) |  [4x Budmen PETG 0.6mm](https://github.com/CRASHSpace/COVID-19-3dprints/raw/master/printfarm/MP10/0.6%20Nozzle/PETG/PETG_06_4XshieldV5_MP10.gcode) | [4x Budmen PLA 0.6mm](https://github.com/CRASHSpace/COVID-19-3dprints/raw/master/printfarm/MP10/0.6%20Nozzle/PLA/MP10_4X_shieldV5_0.6_Test.gcode) |  | [2x Budmen PLA 0.4mm](https://github.com/CRASHSpace/COVID-19-3dprints/raw/master/printfarm/MP10_Mini/0.4%20Nozzle/PLA/PLA_04_108_shieldV5_r042120.gcode)   
0.75" Strap Locks | |[72 Straplocks PLA](https://github.com/CRASHSpace/COVID-19-3dprints/raw/master/printfarm/MP10/0.4%20Nozzle/PLA/PLA_04_72Xstrap_lock_MP10.gcode) | | | |[42x Straplocks PLA](https://github.com/CRASHSpace/COVID-19-3dprints/raw/master/printfarm/MP10/0.4%20Nozzle/PLA/PLA_04_42X_straplock_mini.gcode)

## Setup
NOTE! When you turn off the printer, it can lose it's Z-Offset. Make sure you check this after any power cycle.

## Cleaning
Clean the nozzle while it is heating up -- MORE INFORMATION TO FOLLOW

## Manual level process (tramming the bed)
You need to manually level the bed before printing!
- Zero out the system
  - Set the Z-Offset to 0 (Move -> Tune)
  - Pull print head out of seated position (this ensures nozzle cannot crash into bed and forces the use of mechanical limit switch)
  - Initiate Auto-Level from the touch screen (this will go over the bed using the mechanical level switch and zero out all mesh leveling data)
- Perform manual leveling
  - Lower the bed by tightening the 4 leveling knobs to ensure nozzle will not crash into bed during the leveling process (they are upside down, so remember righty tighty is relative :)
  - Ensure nozzle is clear of any ooze and place head back into place
  - Select the Manual Level Code from the print menu
  - The system will wait for the bed to heat up before continuing
    - The head will then go near each of the leveling knobs and lower to 0.28mm. Use your favorite leveling paper that is near this to check for friction and adjust at each stop
- When complete plug in the leveling probe and perform auto-leveling with bed preheated to printing temps
- Set the Z-offset upon the start of the next print

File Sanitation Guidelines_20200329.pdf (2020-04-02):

Requests for sanitary creation of face shields:

1. Please do not work on any face shields if you are feeling even slightly ill or have felt ill recently. If possible, take your temperature prior to working on face shields and do not work on shields if your temperature is >100.0˚F.
2. Minimize the number of people working on creation and assembly. Although we are grateful for all those who want to volunteer, please include the fewest number of people who can efficiently produce the face shields.
3. If you have cleaning supplies available, please sanitize work surfaces and equipment prior to creating or assembling face shields. Thoroughly wash your hands prior to beginning work and at regular intervals during your work, particularly after eating, coughing or sneezing, or using the bathroom. If you have access to gloves and face masks, please wear them while producing and assembling face shields.
4. Once the shields have been produced and assembled, please handle them as little as possible and pack them into cardboard boxes. Seal the box with packing tape and attach the provided cover sheet to the outside of the box.

Thank you for your assistance in keeping our front-line staff as safe and healthy as possible!

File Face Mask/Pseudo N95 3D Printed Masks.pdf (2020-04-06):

Pseudo N95 3D Printed Masks – Steps for finishing:

After printing you should have three parts.

1. The body
2. The hatch
3. The nose cap

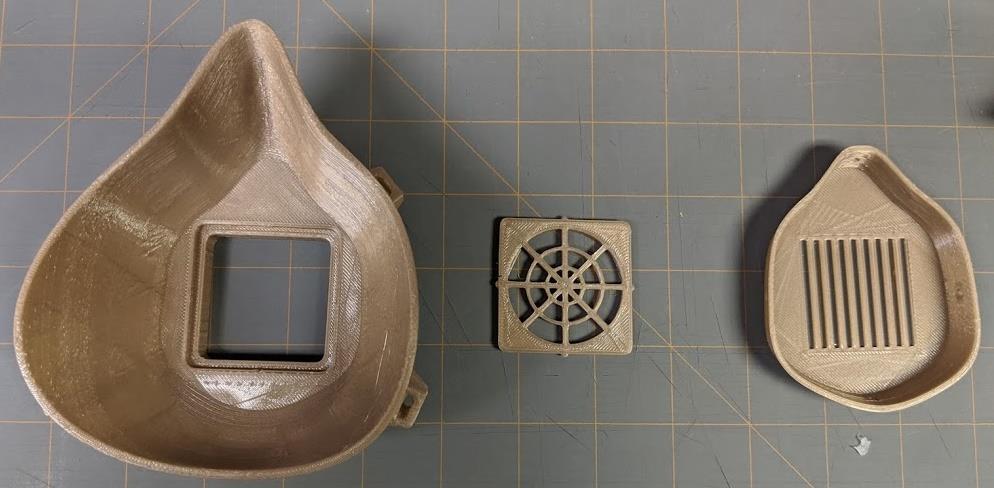
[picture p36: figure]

Figure 1: 3D printed parts from left to right (1) Body, (2) Hatch, and (3) Nose Cap

Step 1: Cut weather stripping to length

We are using Frost King D-profile 5/16 x 1/4 inch Self-Stick Weatherseal.

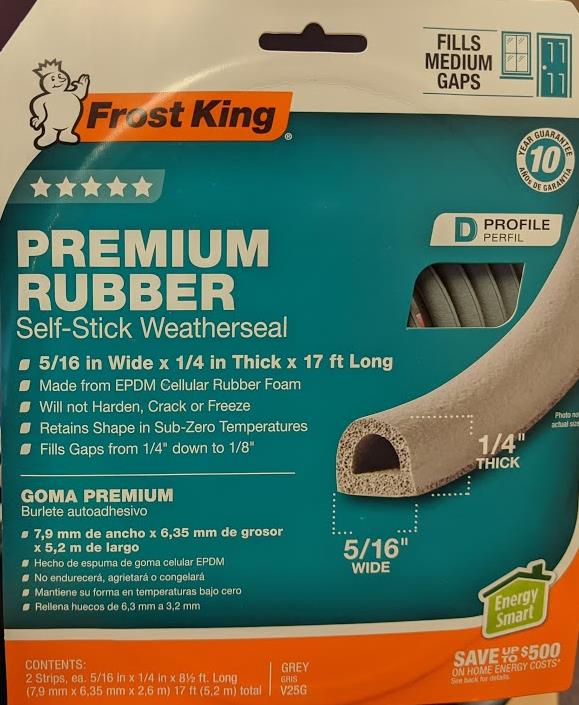
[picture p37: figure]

Cut weatherseal to the following dimensions:

- Medium masks: 14.5 inches
- Large masks (Version 0): 15.0 inches
- Large masks(Version 2L): 15.5 inches

We are using DAP Weldwood Contact Cement

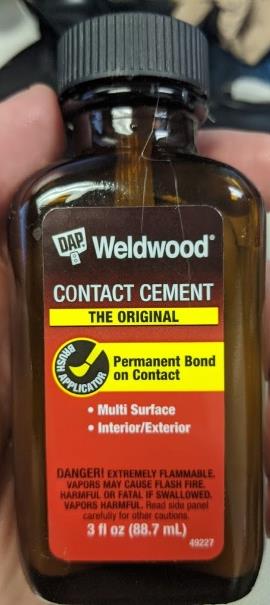
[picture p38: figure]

Use contact cement on the ends of the weatherseal. Let sit for 5-10 minutes. Touch both ends to form a loop.

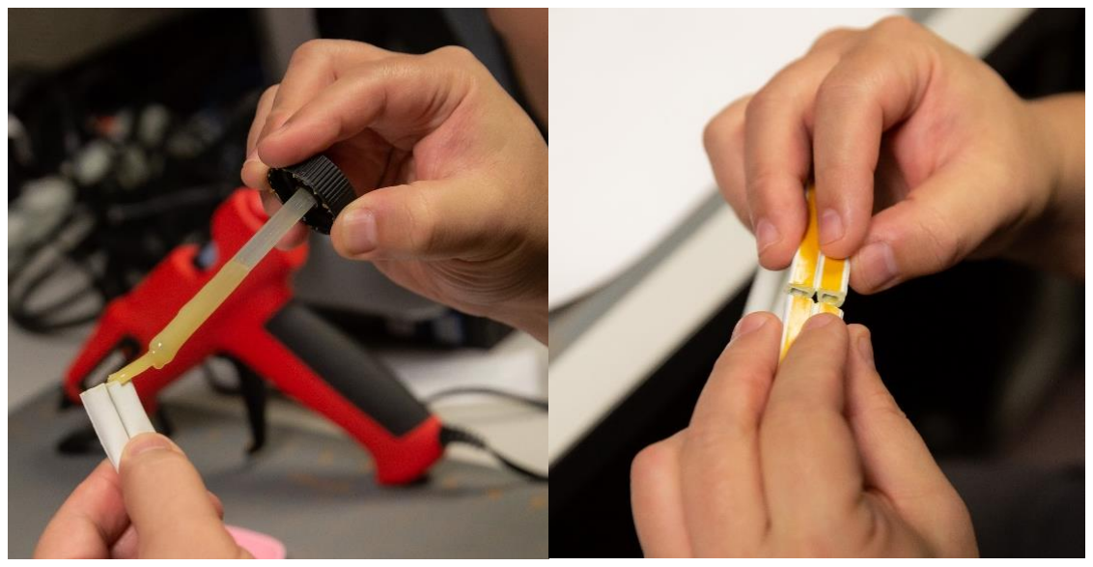
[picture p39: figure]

When dry, separate weather stripping into two loops

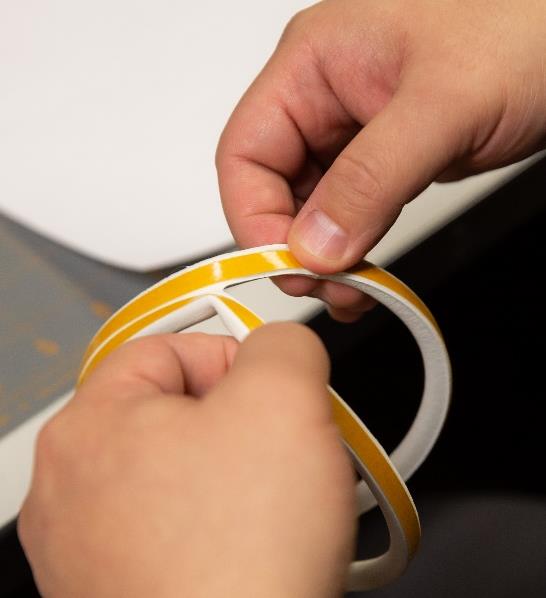
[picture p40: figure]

Peal the backing off the adhesive to start applying to the Mask Body.

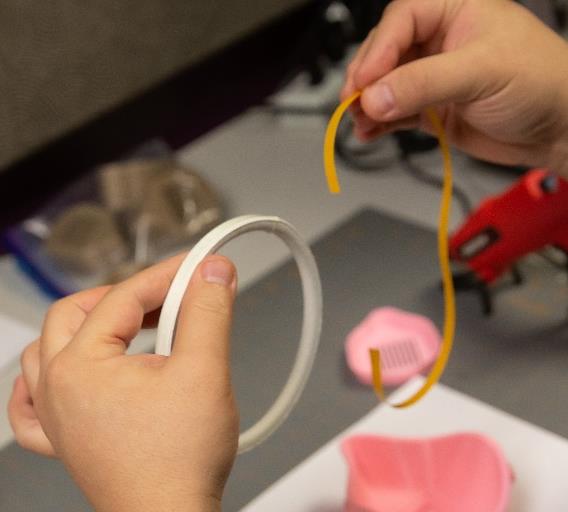
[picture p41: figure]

Start by putting the contact cemented end to the bottom of the Body.

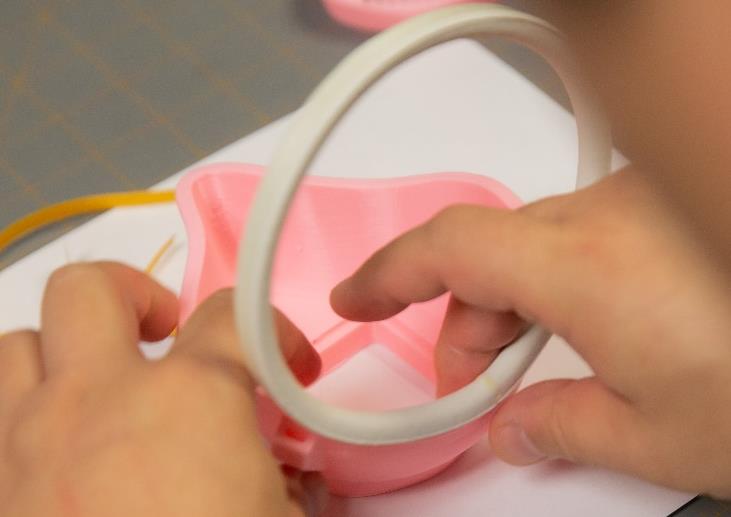
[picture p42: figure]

Work around the parameter touching down the adhesive to the ledge. Try to make a slight overhand on the inner part of the mask and a larger overhang on the outer portion of the mask.

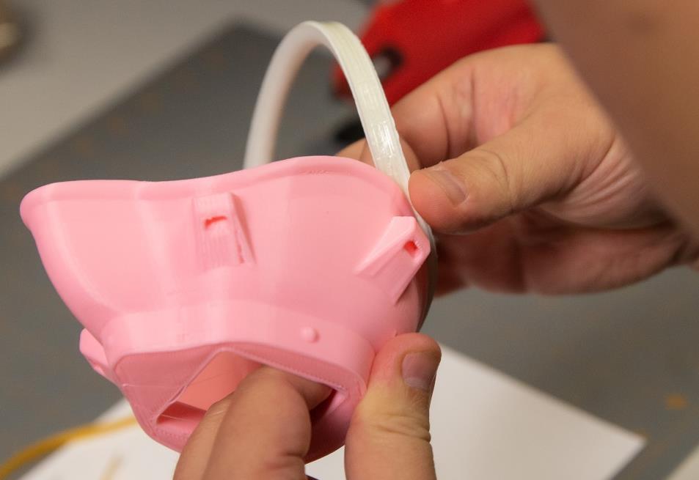
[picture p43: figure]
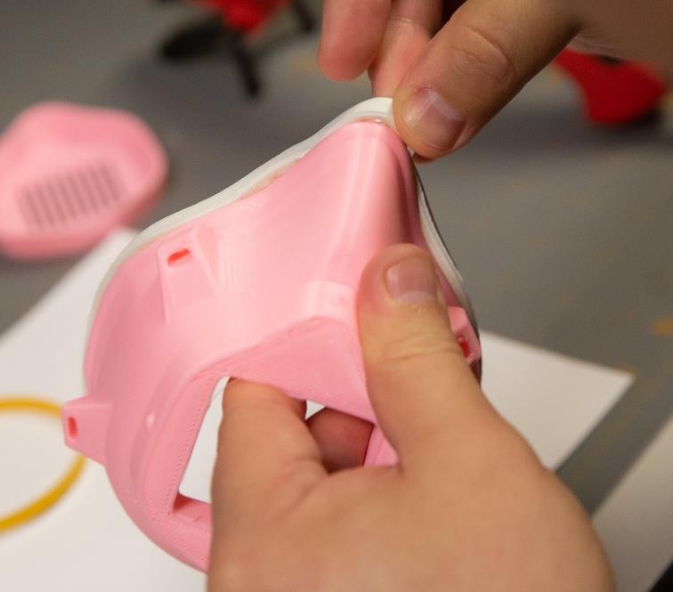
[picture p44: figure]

Pay close attention to the bridge of the nose interface for tight seal

Begin hot gluing. The recommended technique is two part. First lay a thick bead of hot glue at the seam between the mask body and weather stripping.

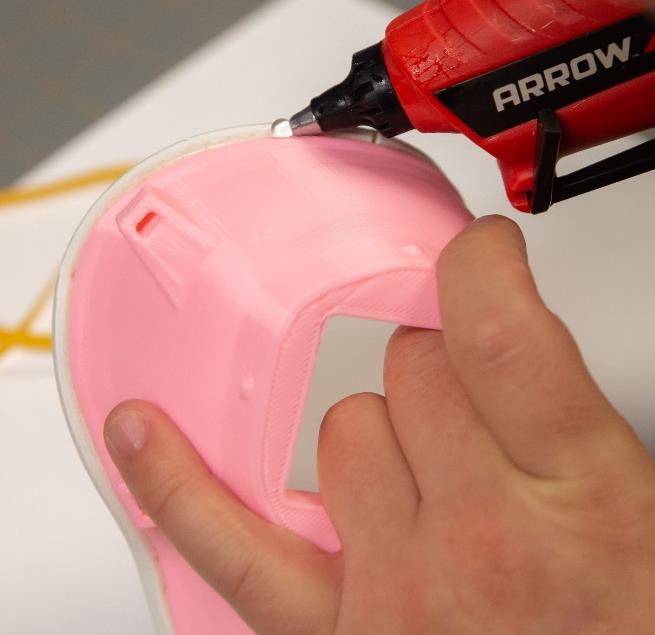
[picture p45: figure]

Then take the tip of the glue gun to evenly spread the glue into a wide swath forming an airtight seal between the mask and the weather stripping.

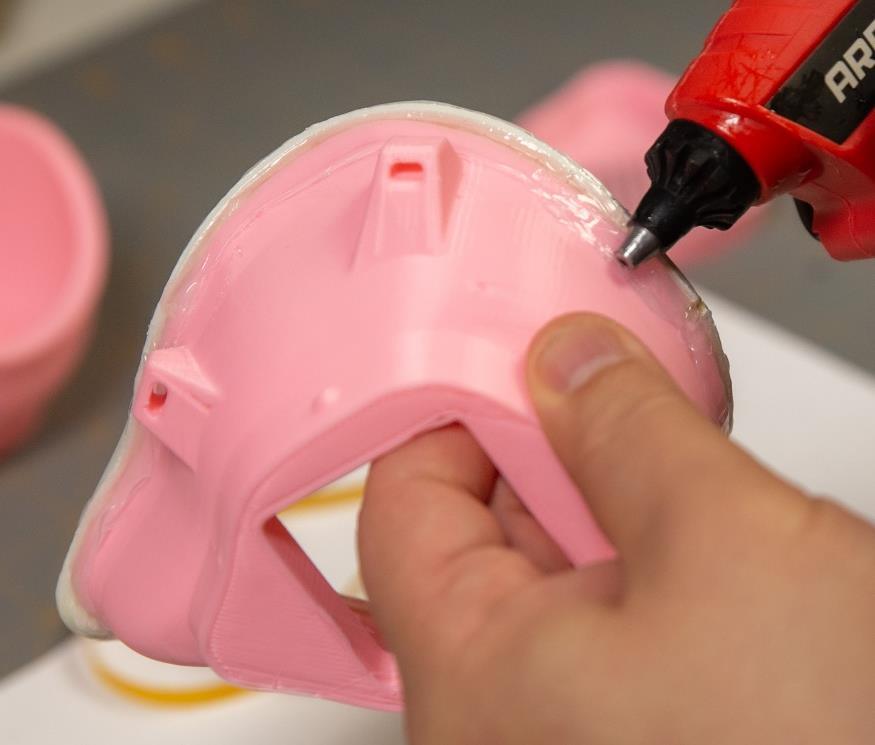
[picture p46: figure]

For filtering material we are using Honeywell HEPAClean Air Purifier Filter model HRF201B

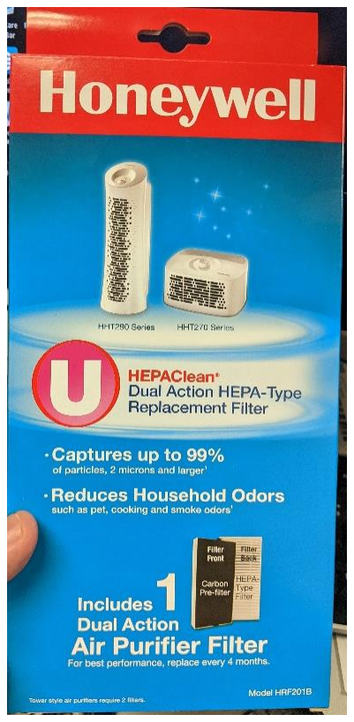
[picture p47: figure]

Remove the black Carbon Pre-Filter from the front of the filter. Gently break open the top edge of the filter. Gently detach the sides of the HEPA filter. Keep central filter intact.

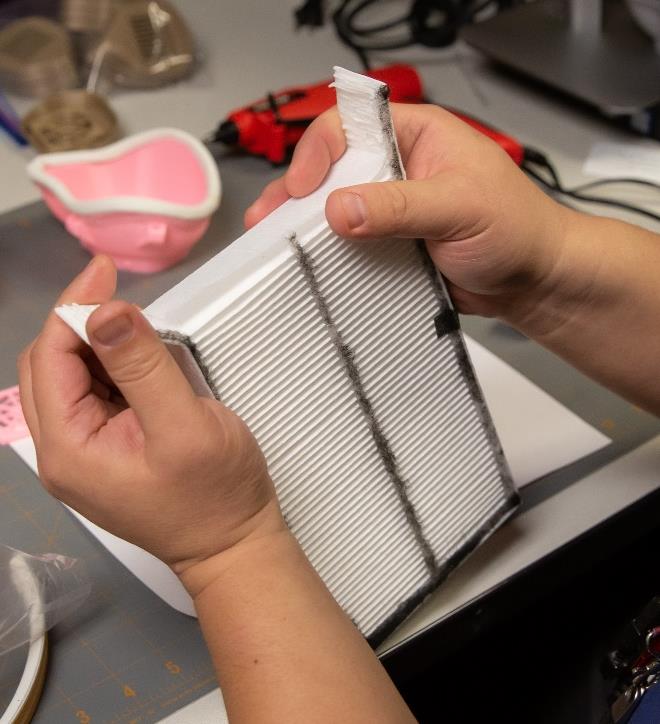
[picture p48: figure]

Cut the HEPA filter into 1 fold sections. The end piece should have a fold in the middle of the filter.

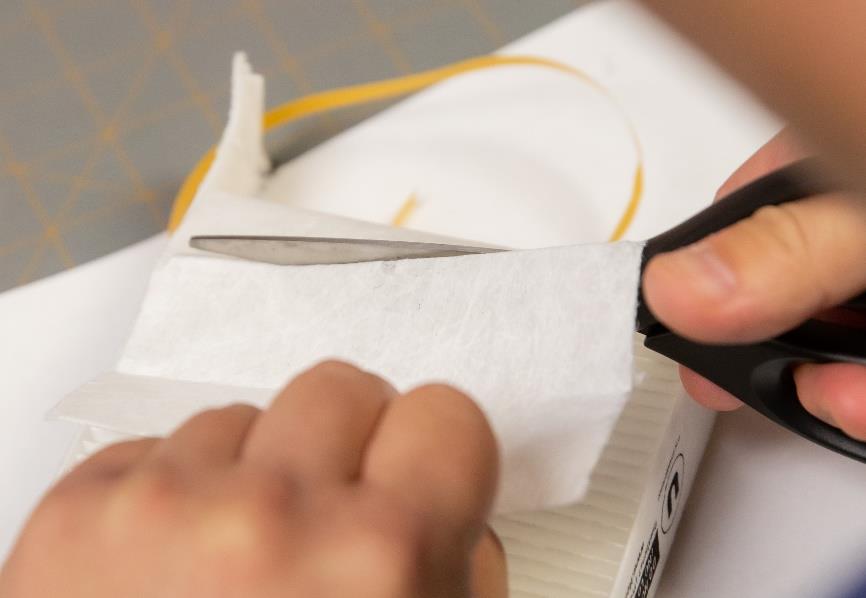
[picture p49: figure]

Fold cut sheet in half and cut. This will leave you 2 squares of filter material.

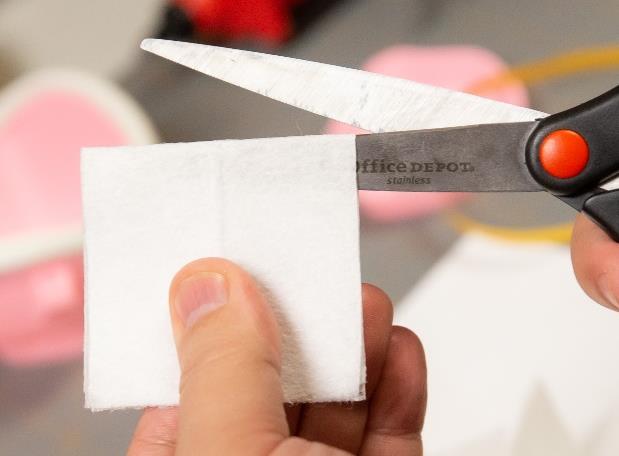
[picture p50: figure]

Each square should be enough to cover the Hatch with a generous border around.

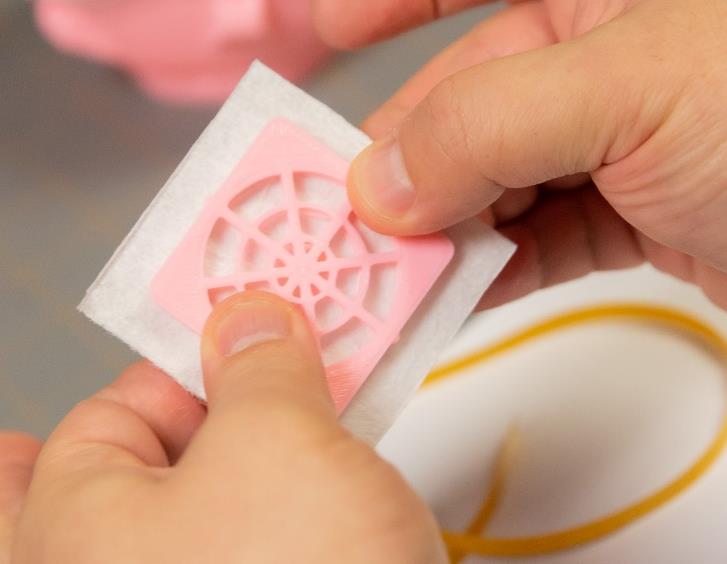
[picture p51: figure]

Place filter into the open in the Mask Body. Apply pressure to fit Hatch into opening. The fit is very tight. Consider print multiple Hatches in case one breaks.

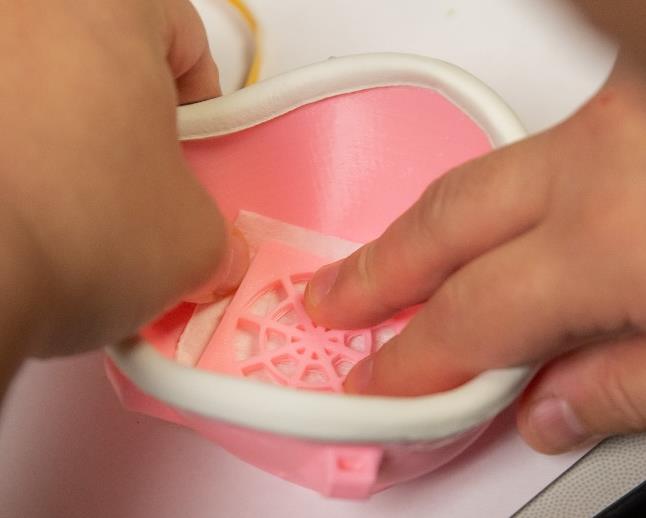
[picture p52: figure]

If needed, use a persuader to ensure tight fit. Be careful not to tear the filter or break the Hatch

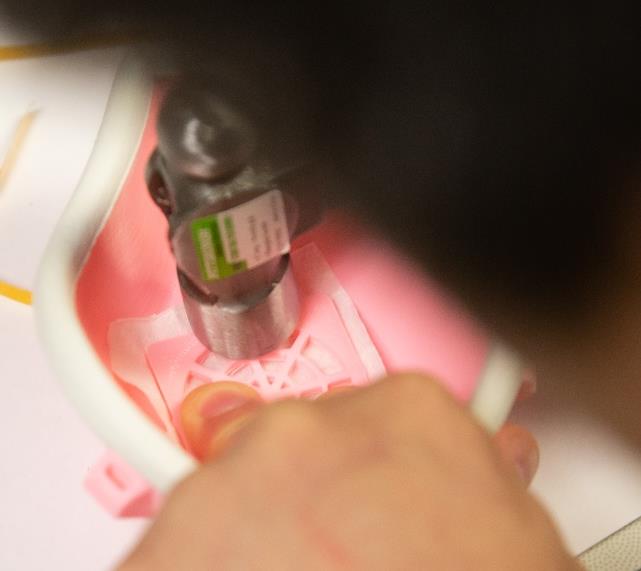
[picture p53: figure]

A well seated filter should see the Hatch nearly flush with the Mask Body.

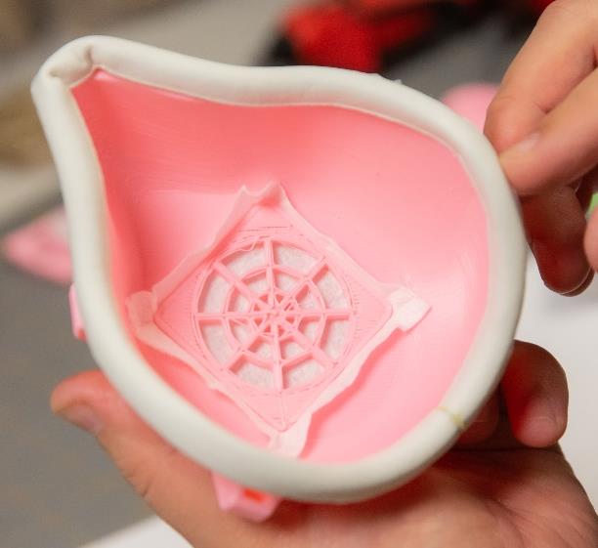
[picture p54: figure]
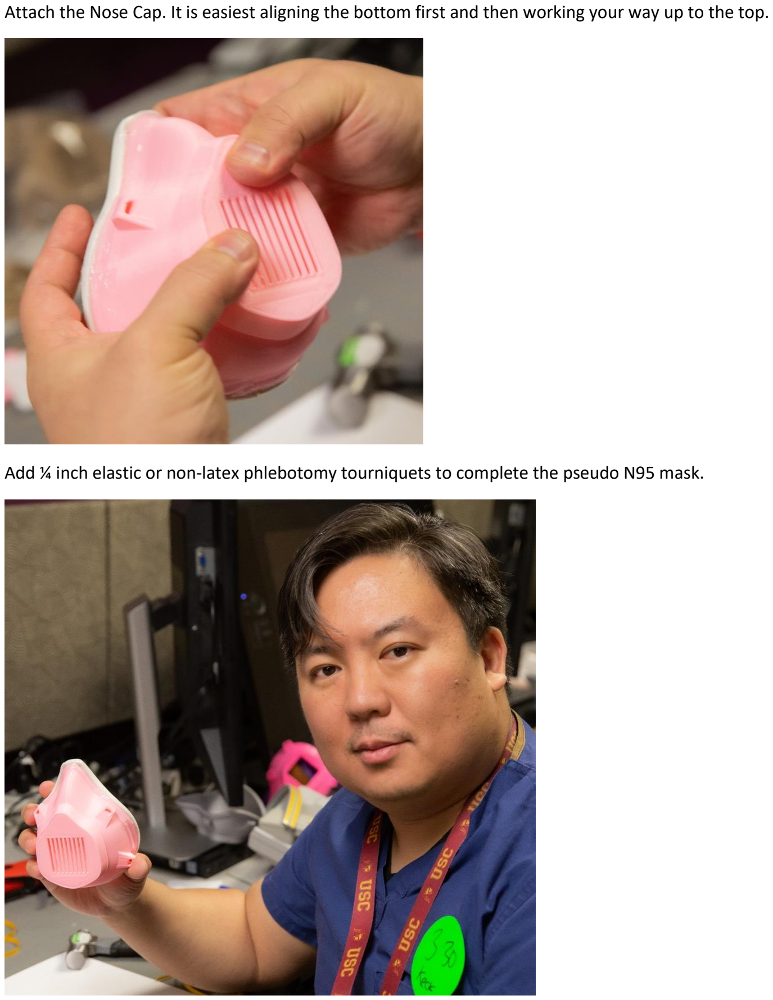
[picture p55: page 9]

Attach the Nose Cap. It is easiest aligning the bottom first and then working your way up to the top.

Add ¼ inch elastic or non-latex phlebotomy tourniquets to complete the pseudo N95 mask.

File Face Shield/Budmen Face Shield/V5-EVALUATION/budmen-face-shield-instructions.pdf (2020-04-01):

# 3D FACE SHIELD

## FABRICATION + ASSEMBLY INSTRUCTIONS

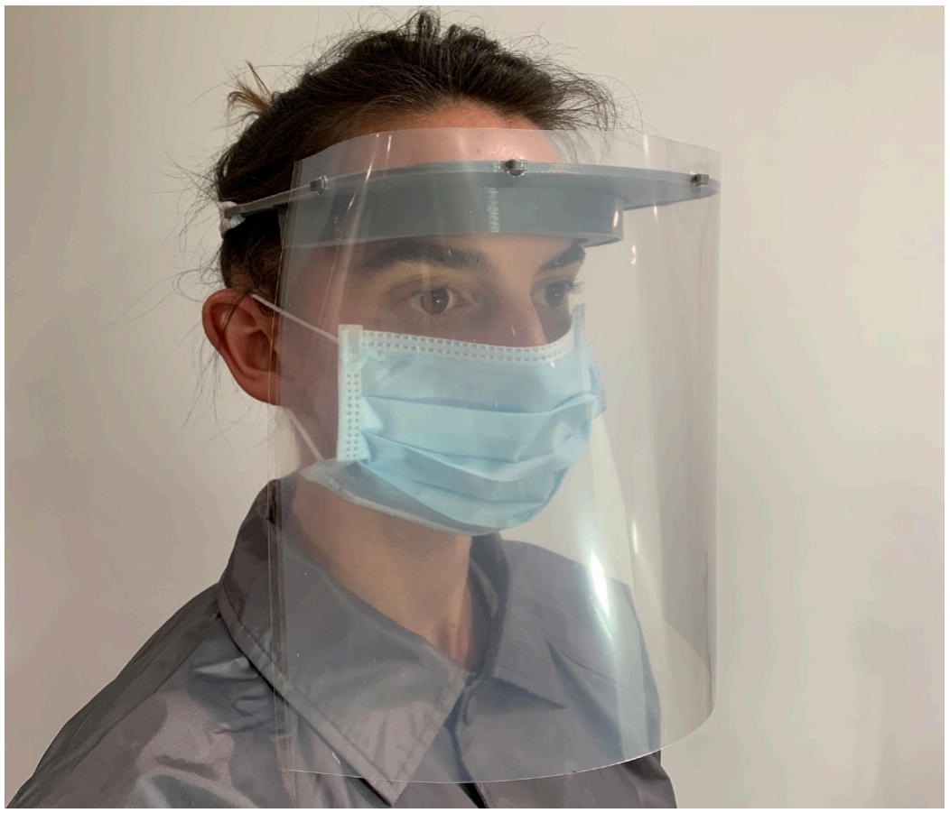
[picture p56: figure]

### 1 OF 11

## BILL OF MATERIALS

MATERIALS
Foam Tape 3/4in wide x 1/2in thick - cut to 9.5in long .005in thick poly sheet - cut to 12in x 9in rectangles Material: PET-G, Acetate, or other clear impermeable material Elastic Band - 1/2in wide - cut to 31in long
PLA Filament for 3D Printer
Super Glue
Rubbing Alcohol and other disinfectants Polybags

Tape

TOOLS
3D Printer
.25in hole punch
Razor blade or scissors
Vinyl Gloves
Face Mask

### 2 OF 11

## BILL OF MATERIALS

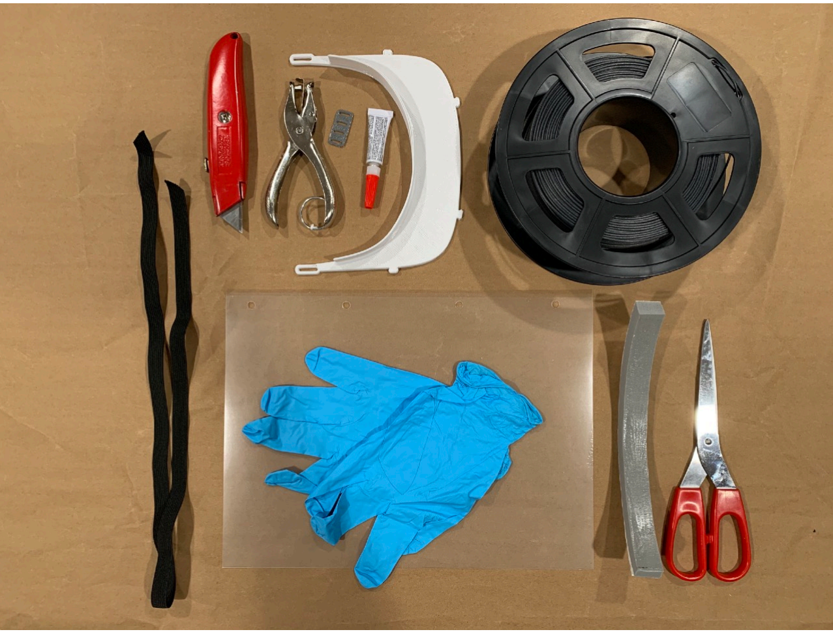
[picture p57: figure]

All materials, parts, and tools needed to assemble the 3D face shield.

### 3 OF 11

## ASSEMBLY INSTRUCT IONS

### STEP 1:

3D Print both the face-shield.stl and strap-lock.stl. Orient both 3D models to print flat on the build platform. We recommend printing both models with as large a layer height as possible to expedite the print time.

### SUGGESTED PRINT PARAMETERS:

Layer Height: 0.3mm
Infill: 10%
Perimeters: 2
Bottom Solid Layers: 2
Top Solid Layers: 2

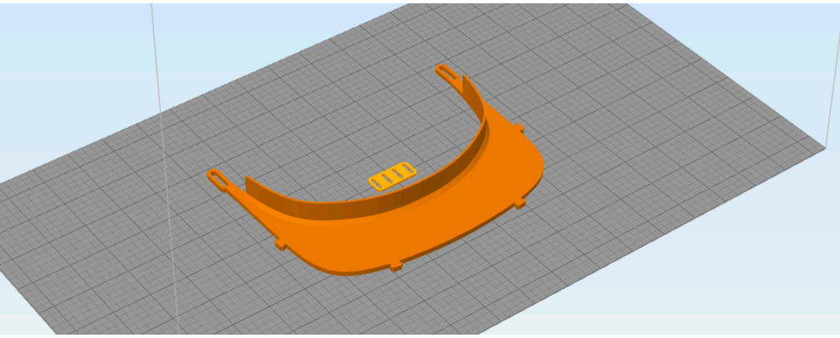
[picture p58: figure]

3D Models oriented flat side down on build plate in slicing software

### 4 OF 11

### STEP 2:

Thread the elastic band through outside loops of 3D printed visor.

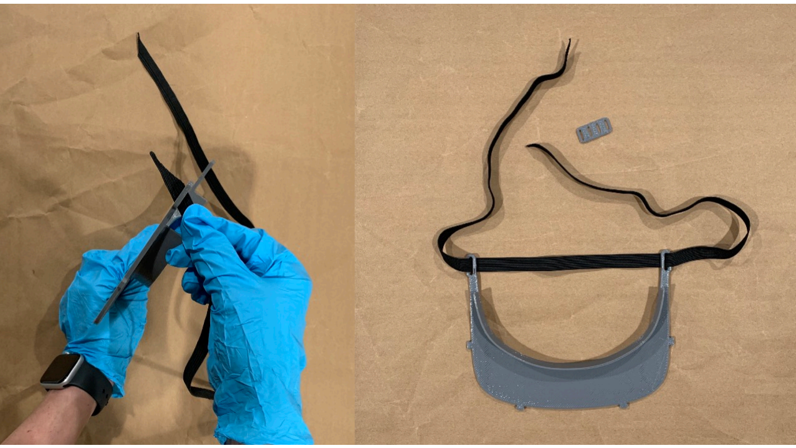
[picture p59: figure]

### 5 OF 11

### STEP 3:

There are four holes in the strap lock. Thread the elastic up through the third hole and down through the fourth. Thread the other end of the elastic of through the second hole and down through the first.

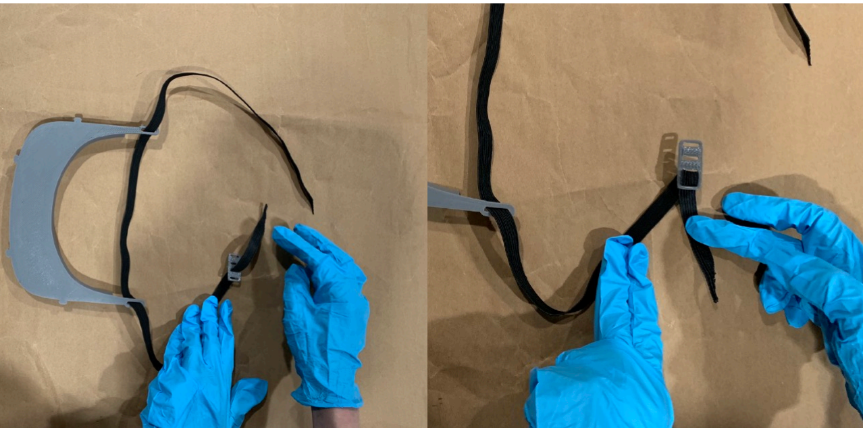
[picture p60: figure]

### 6 OF 11

### STEP 4:

Put a thin strip of super glue along the inside visor panel. Attach the sticky side of the foam to the visor. Put firm pressure for ten seconds on the foam so the glue can fully adhere to the visor.

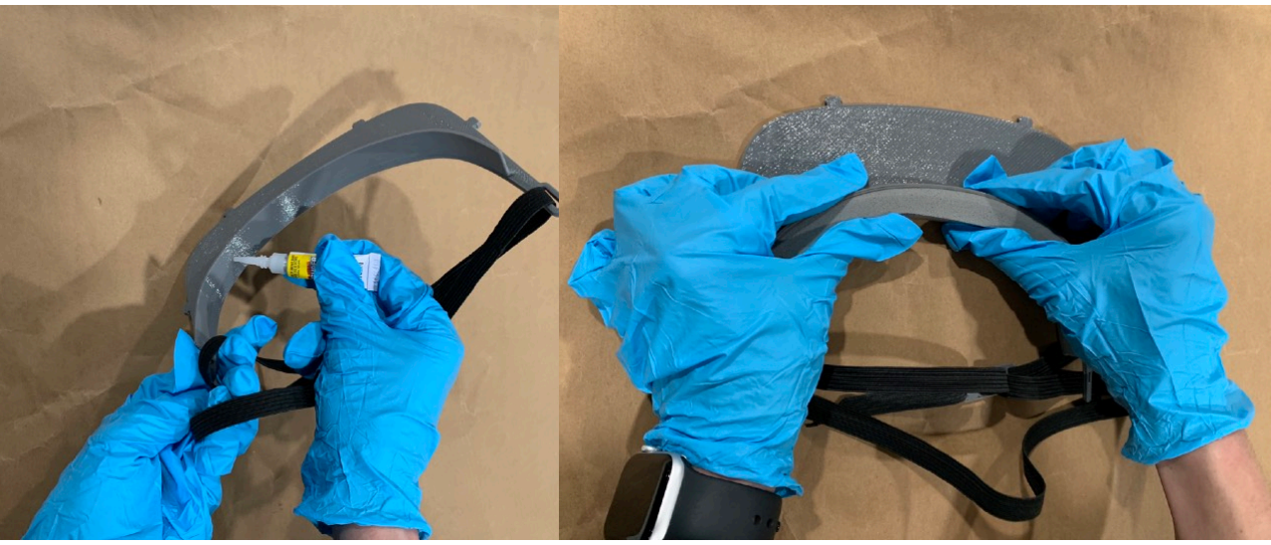
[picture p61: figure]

### 7 OF 11

### STEP 5:

Align the poly sheet to the edge of the hole punch template. Make four holes using the template for accurate placement.

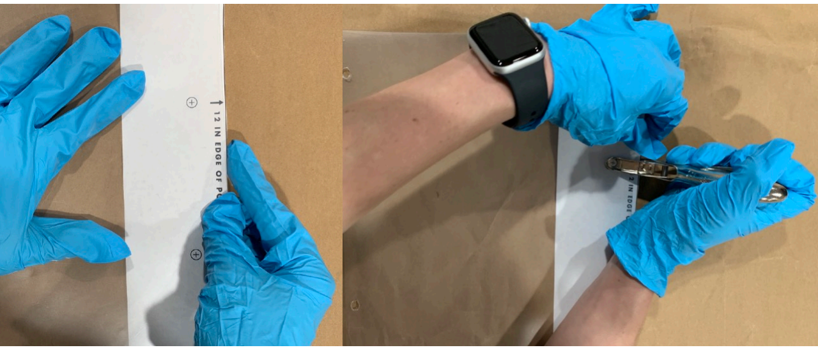
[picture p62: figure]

### 8 OF 11

### STEP 6:

Place the unassembled poly sheet and visor into a clean poly bag and seal. Photo below is the fully assembled 3D face shield.

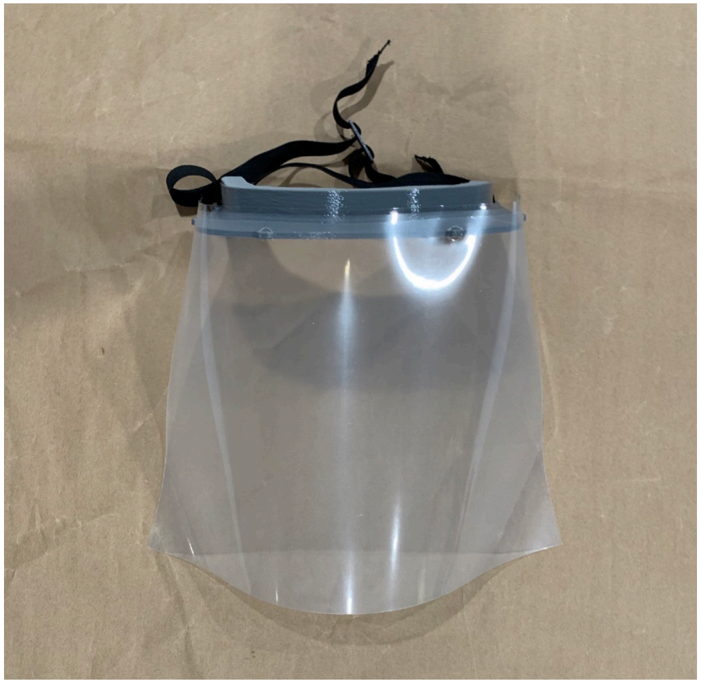
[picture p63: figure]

### 9 OF 11

Release, Waiver of Liability, Defense, Indemnification and Hold Harmless Agreement

You acknowledge that you understand that Isaac Budmen Industries LLC (“Budmen”) is acting as a good samaritan and an independent volunteer providing dissemination of a 3D design for the manufacture of face shields. We do not certify the design or components operate properly or satisfy any regulatory requirements. This Release, Waiver of Liability, Defense, Indemnification and Hold Harmless Agreement (“Agreement”) is meant to reflect the fact that Budmen offers the design as an experimental device, without warranty of any kind. The person signing below (“You”) is either the individual recipient of the design if the individual recipient is an adult under the laws of the relevant jurisdiction or the parent or legal guardian of the child if the individual recipient is a child under the laws of the relevant jurisdiction.

You agree that the design provided to You by Budmen or by any individual associated with Budmen is provided “AS IS” and without representations or warranties of any kind, express or implied, and is intended to be a gift. By accepting the design, you further acknowledge that such design has not been evaluated or approved by any regulatory authority.

You understand that the design furnished by Budmen is meant to benefit society, and is not intended, and shall not be used, for commercial use. If You are an adult under the laws of the relevant jurisdiction and are the individual recipient, you acknowledge that You understand the potential risks of the use of the design and expressly assume such risks. If the individual recipient is a child under the laws of the relevant jurisdiction, You represent that You are the parent or legal guardian of the child and that You understand the potential risks of the use of the design and expressly assume such risks on behalf of the individual recipient.

Furthermore, You (either for yourself or your child) release and forever discharge Budmen from any and all liability for acts or omissions— including negligent acts or omissions— causing damage, loss, injury, or death to the individual recipient or others from the use of the design. You agree to defend, indemnify and hold Budmen harmless from any and all liability or loss—including liability for negligence—arising in conjunction with or resulting from the individual recipient’s use of the design (including all attorney’s fees and expenses incurred by Budmen).

You further understand and agree that Budmen and any individual associated with Budmen shall not be liable for any injuries or damages, including any consequential, incidental, indirect, punitive or special damages, resulting from or arising out of the use of the design provided by Budmen or any individual associated with Budmen.

### 10 OF 11

Any information provided by Budmen and any individual associated with Budmen is not intended to be relied upon to protect from, diagnose or treat a health problem or disease, and Budmen makes no claims regarding the design or the components. You should consider consultation with a qualified health care provider prior to providing face shields manufactured pursuant to the design. Any statements made by Budmen are for informational purposes only and are not meant to replace the services or recommendations of a physician or other qualified health care practitioner.

You acknowledge that this Agreement is governed by the laws of the State of New York (without reference to its conflict of law provisions) and the parties intend that this Agreement be interpreted as broadly and inclusively as permitted by law. If any portion of this Agreement is found to be invalid for any reason, the remainder of the Agreement shall continue to remain in full force and effect and shall continue to be binding.

By accessing the design, You acknowledge that You have carefully read the foregoing provisions, understand their contents, and agree with and to each and every provision herein.

### 11 OF 11

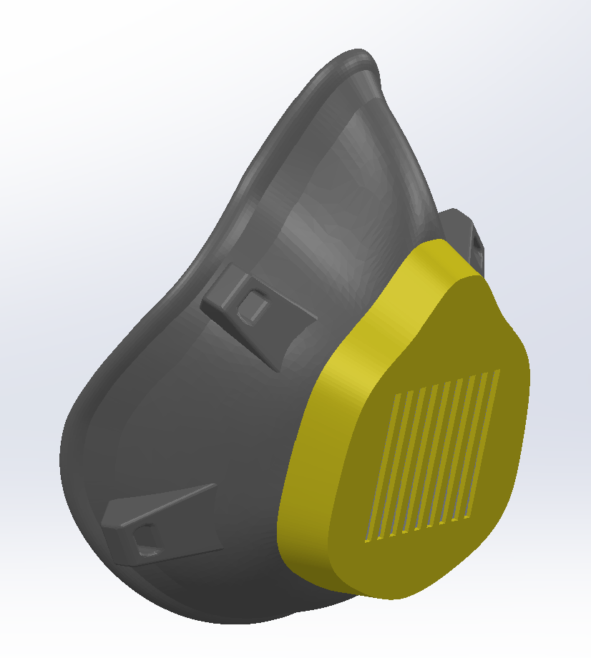
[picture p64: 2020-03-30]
images/USCv2assembled.png

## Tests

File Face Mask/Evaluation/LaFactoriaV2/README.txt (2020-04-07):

COVID-19 MASK v2 (Fast print, no support, filter required) by lafactoria3d on Thingiverse: https://www.thingiverse.com/thing:4225667

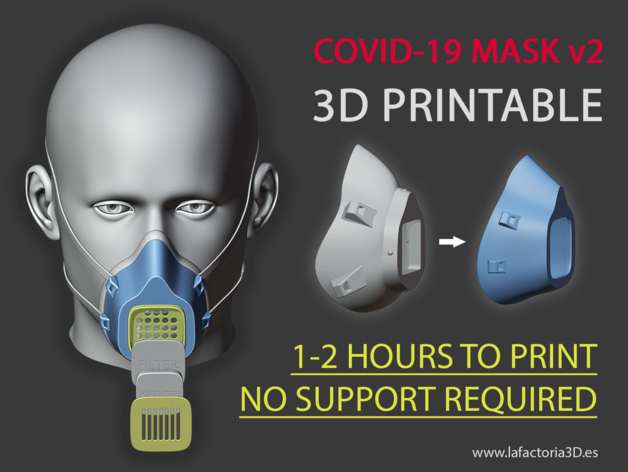
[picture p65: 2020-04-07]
Face Mask/Evaluation/LaFactoriaV2/images/mockup0.png

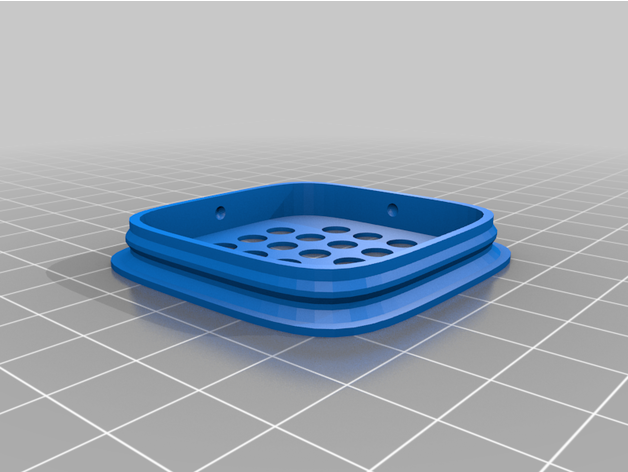
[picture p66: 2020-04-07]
Face Mask/Evaluation/LaFactoriaV2/images/Filter_standard_connector.png

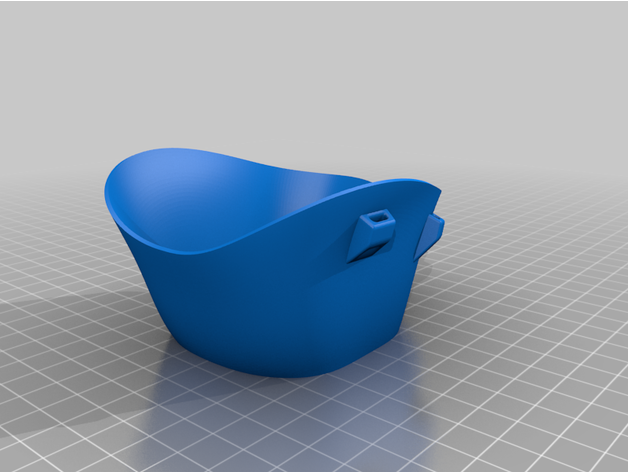
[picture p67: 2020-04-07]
Face Mask/Evaluation/LaFactoriaV2/images/Mask_body_M_wide.png

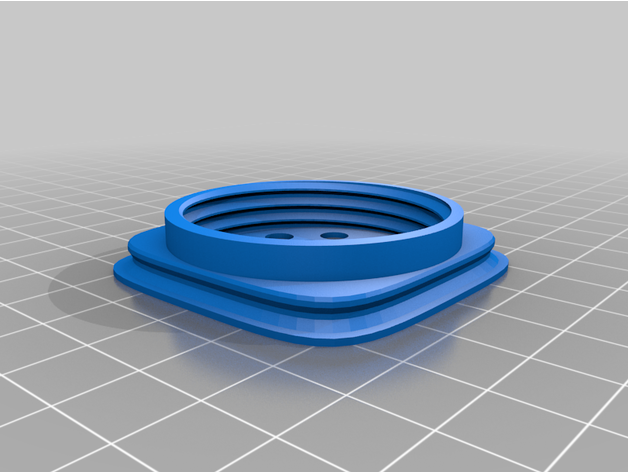
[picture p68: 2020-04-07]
Face Mask/Evaluation/LaFactoriaV2/images/Filter_N95_connector.png

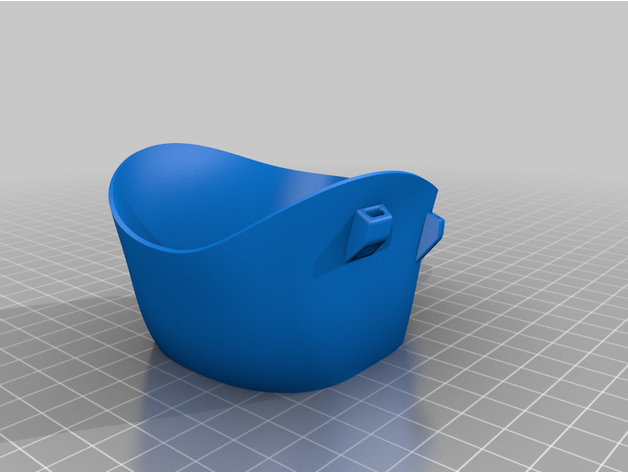
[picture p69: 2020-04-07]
Face Mask/Evaluation/LaFactoriaV2/images/Mask_body_S_wide.png

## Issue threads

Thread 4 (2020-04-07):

### ISSUE TITLE
Versioning Interoperability?

### ISSUE THREAD

**Issue by j3ffgray** [CRASHSpace/COVID-19-3dprints#4]
To confirm, is care being taken to make sure masks made in one version still snap together with previous versions? I just finished printing a run of medium masks, but hadn't begun printing the cap and grid, and am hoping to prevent time and material wastage by printing items that won't couple up.

Are their "patch notes" someplace that describe the updates being made between versions?

**Comment by netkruzer** [comment]
Yes, the older versions of the face mask fit the new grid and new cap. They changed the number of slits on the cap.

**Comment by j3ffgray** [comment]
Great, thanks, just wanted to make sure!

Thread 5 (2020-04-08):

### ISSUE TITLE
Fiberglass in mask filters

### ISSUE THREAD

**Issue by sam598** [CRASHSpace/COVID-19-3dprints#5]
There are some air filters that contain fiberglass and should not be disassembled and used in masks. (https://www.reddit.com/r/3Dprinting/comments/ftmgtp/3d_printing_respirator_masks_be_aware_filters_can/)

Does anyone know if the filters linked in the readme (https://www.amazon.com/Flintar-Replacement-Compatible-Honeywell-HRF201B/dp/B07SQ5NHJ7/ref=sr_1_5?pldnSite=1) contain fiberglass? Should any special precautions be taken when cutting or using these masks? Should all "true-hepa" filters be okay to use?

**Comment by netkruzer** [comment]
I've bought a couple of these packs and taken them apart. They do not have the standard fiberglass in them that other wall type filters have. 

As for other HEPA filters, I can't say for sure. The ones you listed on Amazon only have some glue to deal with.

**Comment by netkruzer** [comment]
Also, these HEPA filters were recommended to us by USC Keck Medicine.

**Comment by sam598** [comment]
Thanks @netkruzer 

I will close this for now. I would be interested to hear if there are any updates or alternative filters.

**Comment by netkruzer** [comment]
It's a good question to ask. Don't want people endangering themselves with the wrong filters.

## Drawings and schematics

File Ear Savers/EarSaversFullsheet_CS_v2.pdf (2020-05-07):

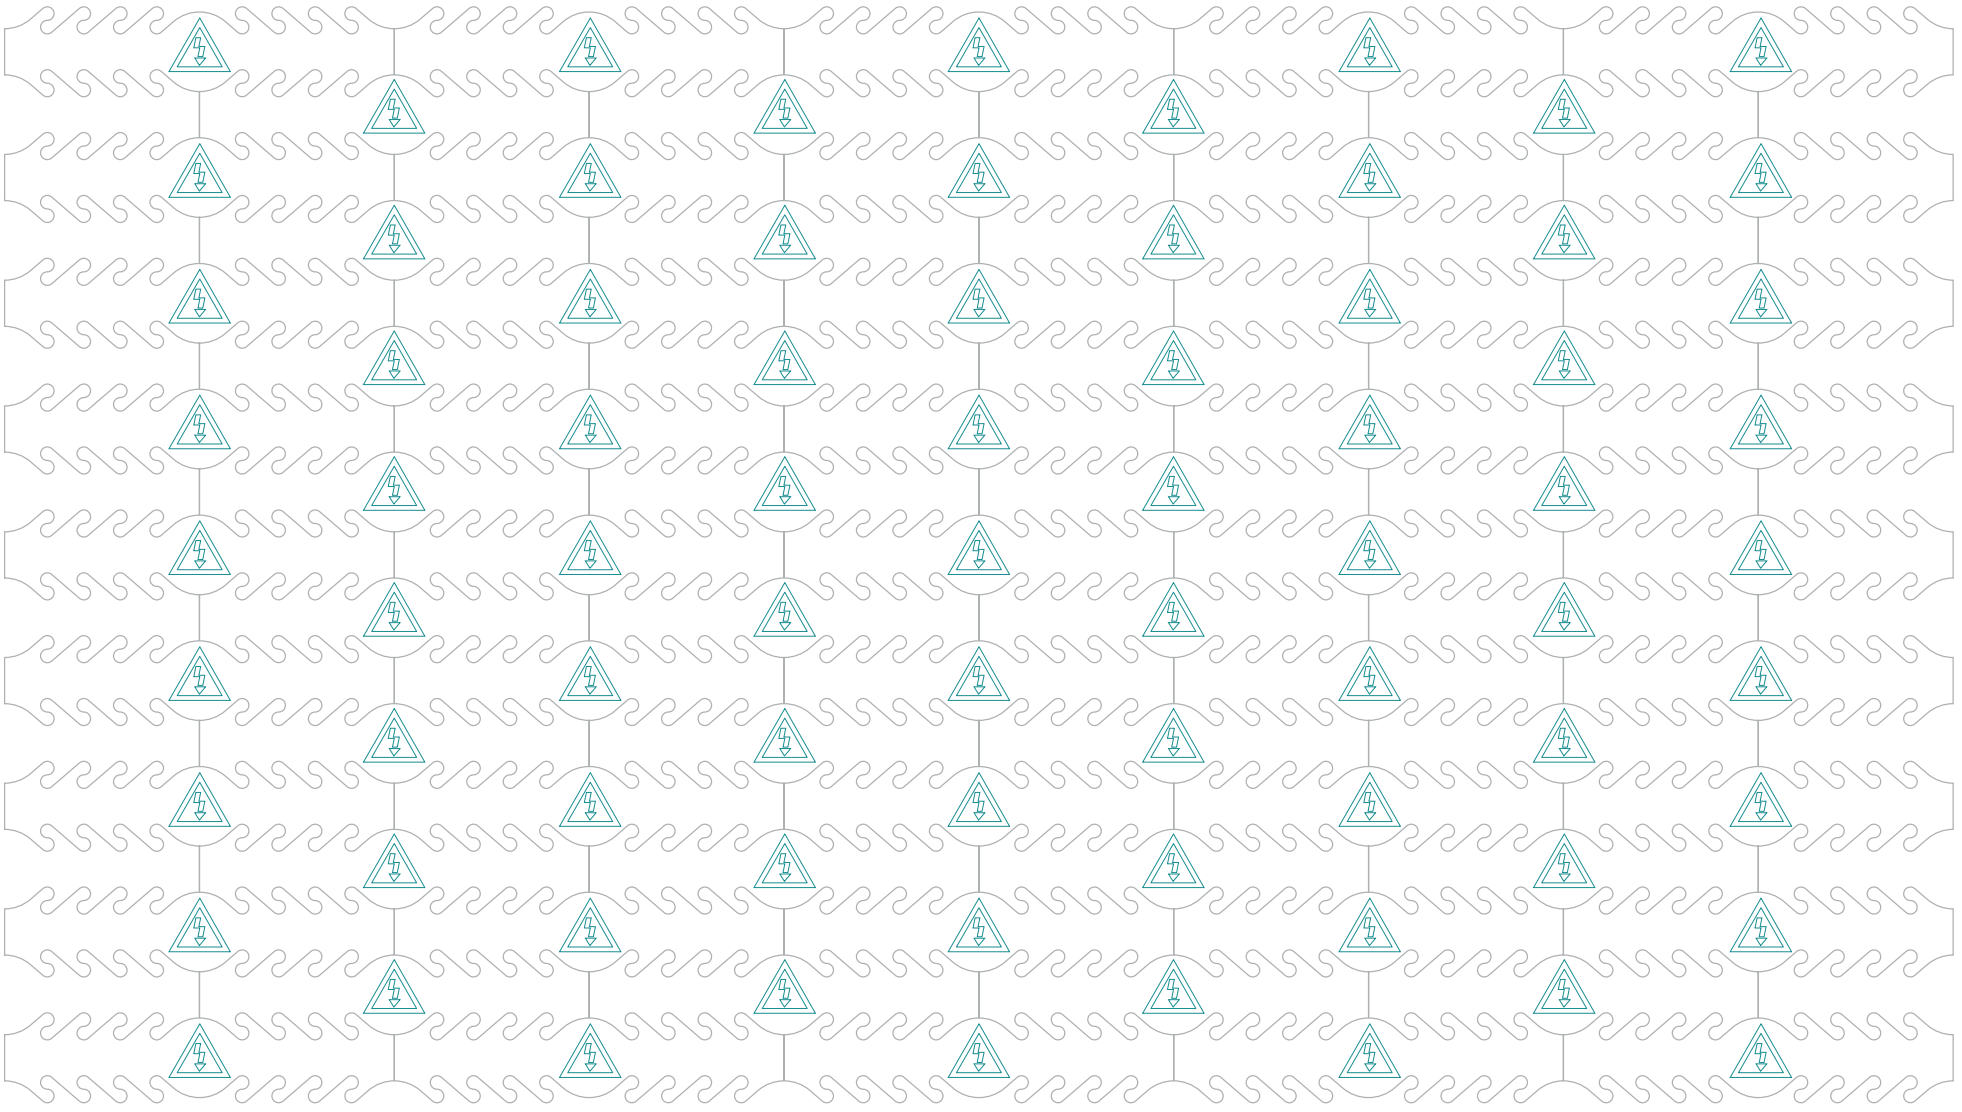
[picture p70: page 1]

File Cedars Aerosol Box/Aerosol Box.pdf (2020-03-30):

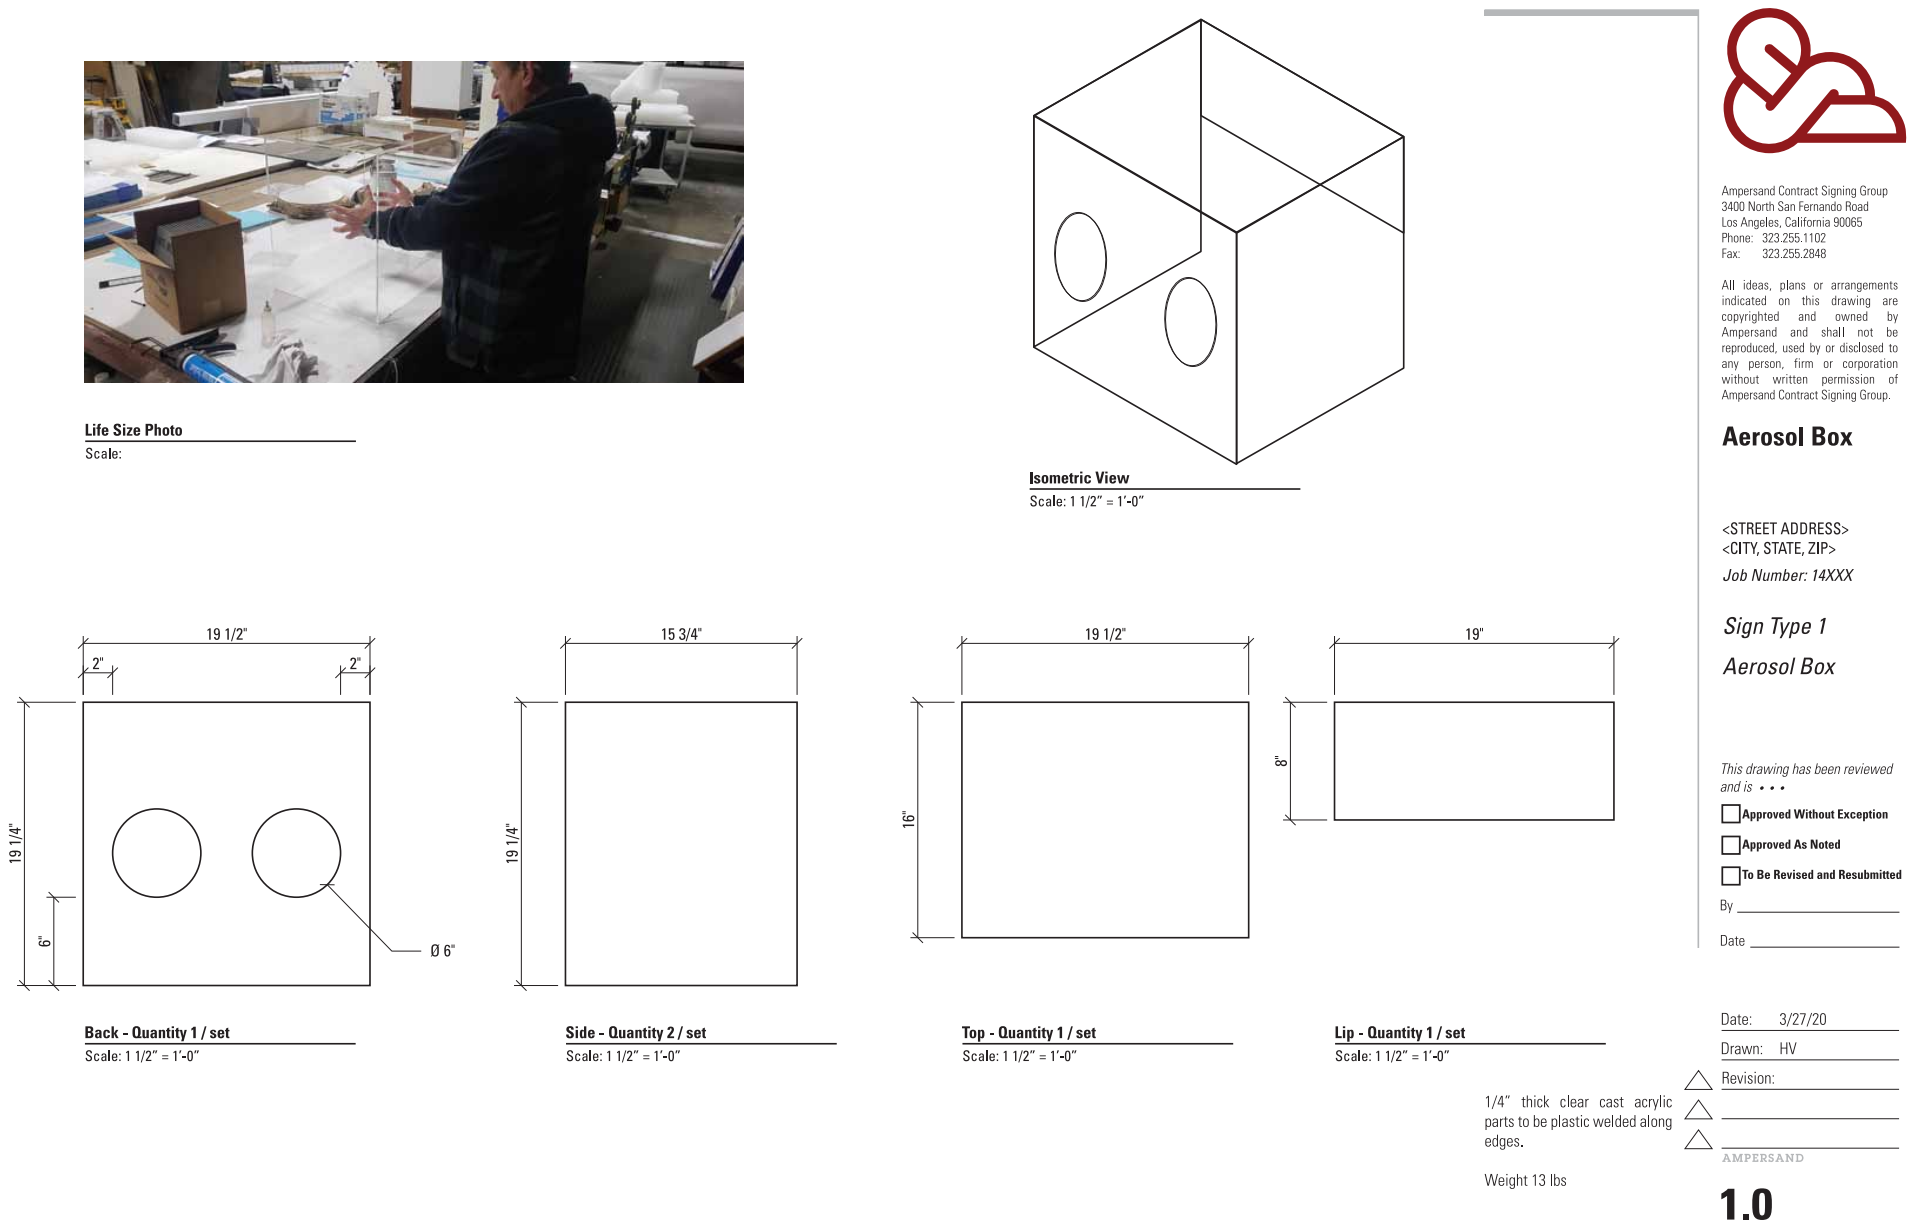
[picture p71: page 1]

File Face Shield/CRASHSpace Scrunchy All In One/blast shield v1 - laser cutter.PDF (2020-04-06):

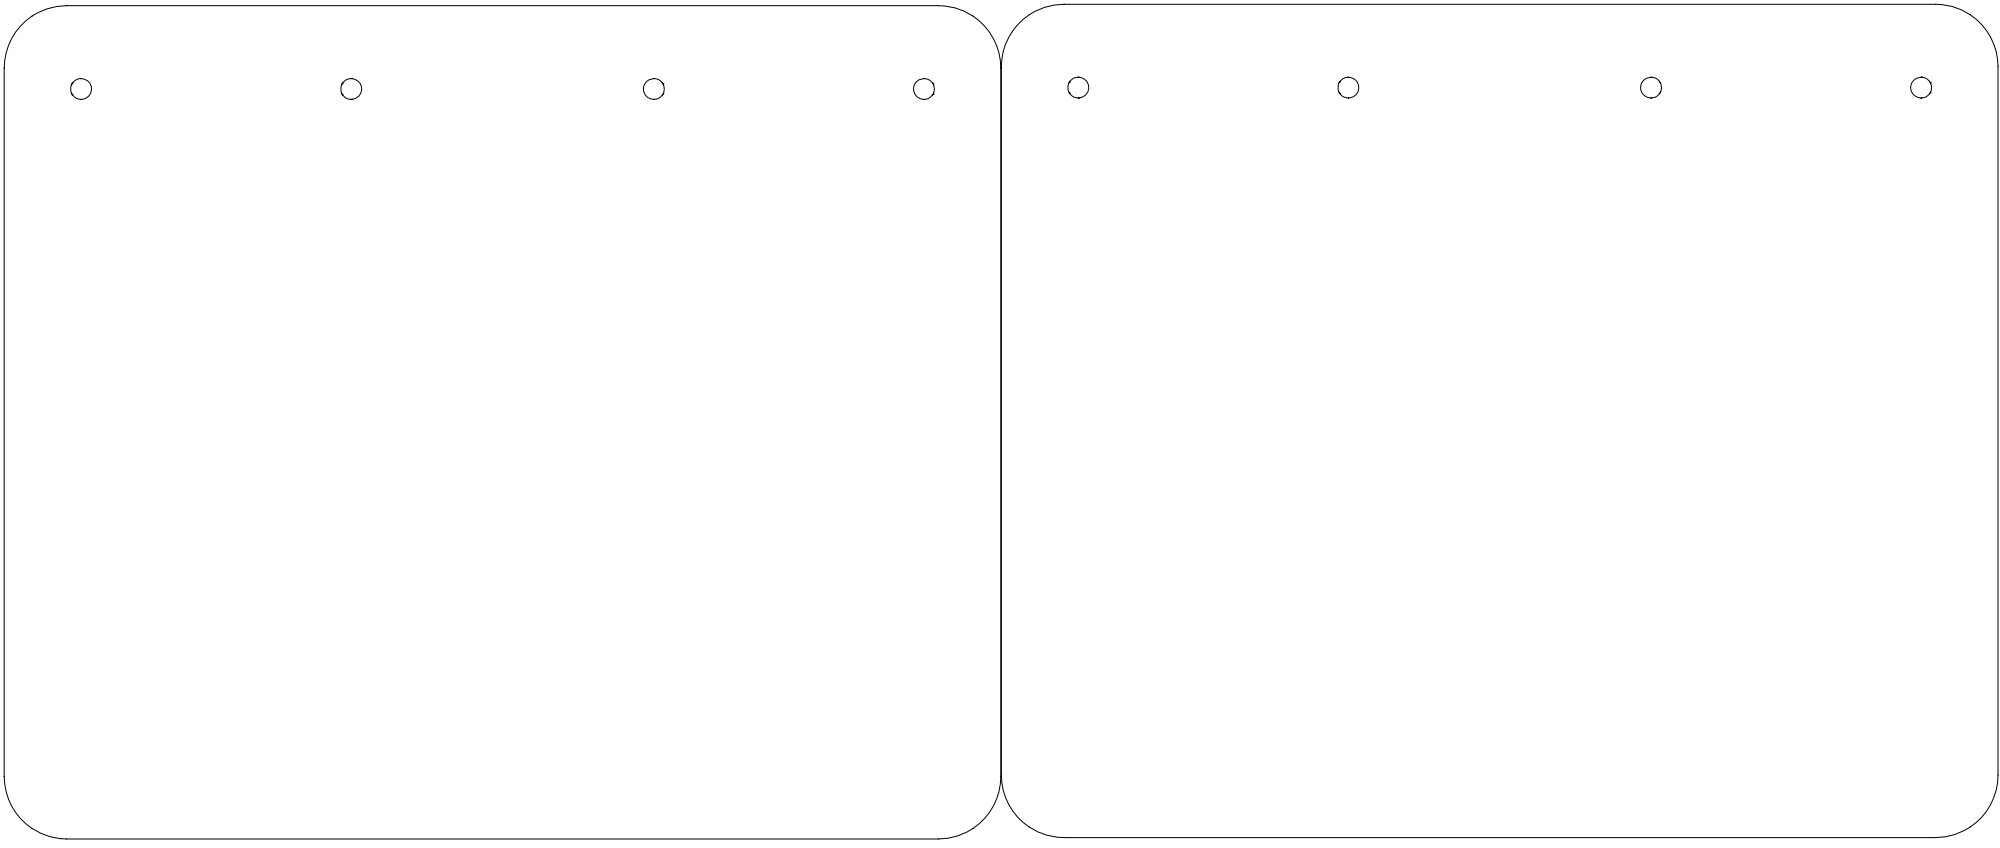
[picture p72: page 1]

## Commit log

2020-03-28 initial files
    [covid_mask_cap.stl, covid_mask_grid.stl]
2020-03-28 update readme and move files to directories
    [covid_mask_cap.stl, covid_mask_grid.stl]
2020-03-28 Add images
    [USC_CovidMask_V1.3mf]
2020-03-29 updated mask files , 2 sizes
    [USCSW-Filtrated_Mask-v2L.stl, USCSW-Filtrated_Mask-v2M.stl, USC_CovidMask_V1.3mf]
2020-03-29 Updated readme dropzone
    [USC_CovidMask_V1.3mf]
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2020-03-30 Added Prusa 3MF
    [Prusa_pre-laid-2xM-1xL-USCSW-Filtrated_Mask-v2.3mf]
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2020-03-31 New Face Shield
    [SMP Face Shield rev3.STEP, SMP Face Shield rev3_SUPPORT.3mf]
2020-04-01 Budmen face shields
    [IC3D Budmen Face Shield V1.stl, IC3D-Budmen-Polysheet-V1.dxf, face-shield.obj, face-shield.step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]
2020-04-01 Budmen face shield v3 - 3mf laid out
    [BudmenV3_2face_shields-Pre-laid-out.3mf, Prusa_pre-laid-2xM-1xL-USCSW-Filtrated_Mask-v2.3mf]
2020-04-01 Budmen face shield v4 - 3mf laid out
    [BudmenV4_2face_shields-Pre-laid-out.3mf]
2020-04-01 Updated SMP Face shield
    [SMP Face Shield rev3.STEP, SMP Face Shield rev3_SUPPORT.3mf]
2020-04-02 renamed file for Windows
    [IC3D-Budmen-Polysheet-V1.dxf]
2020-04-02 Add 3DVerkstanV5 face shield
    [Lasercut-shield-NORTH-AMERICA-6-hole-letter-format.dxf, Visor_Frame_NORTH_AMERICA_letter_6-hole_v5.stl]
2020-04-03 Updated Face Mask links to direct to USC maintained copies
    [USCSW-FMask-Hatch-V2.stl, USCSW-FMask-Nose_Cap_v2..stl]
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2020-04-03 Updated USC Fask Mask files and links
    [Prusa_pre-laid-2xM-1xL-USCSW-Filtrated_Mask-v2.3mf, USCSW-FMask-Hatch-V2.stl, USCSW_Hatch_v2r1.stl, USCSW_Nose_Cap_v2.stl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]
2020-04-06 Add Assembly guidelines
    [USCSW_Hatch_v2r1.stl, USCSW_Nose_Cap_v2.stl]
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2020-04-06 Added Work in Progress USC Budmen v5 & Crashspace Scrunchy - don't print yet
    [CrashspaceScrunchy v1.STL, IC3D-Budmen-Polysheet-V1.dxf, USCBM_Faceshield-V5.stl, USCSW_Hatch_v2r1.stl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]
2020-04-07 Updated Verkstan PDF Guide
    [USCSW_Hatch_v2r1.stl, USCSW_Nose_Cap_v2.stl]
2020-04-07 Lafactoria and California mask evaluation units
    [California Mask - Ridged.stl, California Mask.stl, Filter Frame Slotted Snap.stl, Filter_N95_cap.stl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]
2020-04-07 Update approval
    [BudmenV4_2face_shields-Pre-laid-out.3mf, IC3D Budmen Face Shield V1.stl, IC3D-Budmen-Polysheet-V1.dxf, USCBM_Faceshield-V5.stl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]
2020-04-08 Removed Budmen V4 (Not approved by any recipients)
    [BudmenV4_2face_shields-Pre-laid-out.3mf, IC3D Budmen Face Shield V1.stl, IC3D-Budmen-Polysheet-V1.dxf, polysheet.dxf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]
2020-04-08 Updated sheet templates
    [IC3D-Budmen-Polysheet-V1.dxf, polysheet.dxf]
2020-04-10 renamed Budmen v5 to print
    [USCBM_Faceshield-V5.stl]
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2020-04-13 Crashspace Scrunchy Solidworks files
    [Crashspace Scrunchy v1 Assem.SLDASM, Head Cover cylinder.SLDDRW, Head Cover cylinder.SLDPRT, blast shield v1.SLDDRW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]
2020-04-14 Added Printfarm gcode
    [7hr_shieldV5_PETG_r1.3mf, 7hr_shieldV5_PLA+_r1.3mf]
2020-04-16 Added G-Code for MP10 Mini
    [7hr_shieldV5_PETG_r1.3mf, 7hr_shieldV5_PLA+_r1.3mf]
2020-04-16 Added 3/4" Strap lock to Budmen V5
    [0.75in-strap-lock.stl]
2020-04-17 Updated Shield prints to include nwe strap lock
    Both MP10 and MP10 mini files updated with new strap locks and other minor quality adjustments.
    [7hr_shieldV5_PETG_r1.3mf, 7hr_shieldV5_PLA+_r1.3mf, MINI_shieldV5_r041620_PLA.3mf, MP10_shieldV5_r041620_PLA.3mf]
2020-04-17 Crashspace Scrunchy for Budmen Shield
    [Crashspace_scrunchy-v1rc1-for_Budmen.STL]
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2020-04-18 Added PETG Printfarm Files
    Added PETG print variants with slightly slower speeds, higher temps, and lower cooling.
    Updated MINI print file to include small prime line to mitigate strings on first sections.
    [MINI_shieldV5_r041820_PETG.3mf, MP10_shieldV5_r041820_PETG.3mf]
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2020-04-18 Crashspace Scrunchy Large version
    [Crashspace_scrunchy-Budmen-Largev1.STL]
2020-04-22 Printfarm Update
    Updates to printfarm sliced gcodes. Increased layer thickness to 0.32mm. This reduces print time around 15 minutes each shield. Left previous versions in case any of the printers cannot keep up with 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
    [MINI_shieldV5_r041620_PLA.3mf, MP10_shieldV5_r041620_PLA.3mf]
2020-04-22 20mm strap lock
    [0.75in-strap-lock.stl, 20mm_strap_lock.stl]
2020-04-23 Ear Savers Added
    [CS CutOut Ear Saver.stl]
2020-04-24 Crashspace Scrunchy headband to print
    [Crashspace Scrunchy v1 Assem.SLDASM, CrashspaceScrunchy v1.STL, Crashspace_scrunchy-Budmen-Large.SLDPRT, Crashspace_scrunchy-Budmen-Largev1.STL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]
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2020-04-25 Print farm overhaul
    Restructure folder and filenames. Now incudes sections for nozzle and material variants. Multiple flow output files created for each to cover machine and material variability.
    Still need to create readme.md
    [MINI_shieldV5_r041620_PLA.3mf, MINI_shieldV5_r041820_PETG.3mf, MP10_shieldV5_r041820_PETG.3mf, PETG_04_1XshieldV5_MP10.3mf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]
2020-04-26 Resliced printfarm PETG
    New version of dev Cura fixes a couple issues so all PETG has been resliced. Decided against having lots of extrusion multiplier slices until need arises. Slices uploaded tuned for current stock prin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
    [PETG_04_1XshieldV5_MP10.3mf, PETG_04_4XshieldV5_MP10.3mf, PETG_04_shieldV5_MP10mini.3mf, PETG_06_1XshieldV5_MP10.3mf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]
2020-04-26 Add MP10 72x strap lock PLA files
    Added PLA 72x strap lock files and removed single shield hop variants. Hop is mainly beneficial for multi part builds.
    [PLA_04_72Xstrap_lock_MP10.3mf]
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2020-05-01 Additional PLA and PETG print files. Update MP10 Mini PLA files
    Additional PLA and PETG print files for MP10 0.6 and 0.4mm nozzles. Update to MP10 Mini PLA files. Resliced after discovering strange software artifacts causing uneven surfaces.
    [PETG_04_2XshieldV5_MP10.3mf, PETG_06_2XshieldV5_MP10.3mf, PLA_04_2XshieldV5_MP10.3mf, PLA_04_4XshieldV5_MP10_test.3mf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]
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2020-05-02 Added MP10 PETG 0.4mm 11x Ear saver + 12 strap lock gcode
    Added PETG 0.4mm nozzle gcode for MP10 with 11 earsavers + 12 strap locks. Ear savers were scaled up in the Z direction to give 4 layers at 0.3 layer height. 3 hour print time.
    [PETG_04_11XEarSaver_MP10.3mf]
2020-05-03 Printfarm Update, added 0.6 2X shield
    Update ear saver 0.4 PETG to reduce extrusion. Added 0.6mm PLA 2X shield
    [PLA_06_2XshieldV5_MP10.3mf]
2020-05-03 Add MP10 Mini Ear Saver PETG files
    Add MP10 Mini Ear Saver PETG file with 5x earsavers and 6 strap locks
    [PETG_04_5XEarSaver_MP10mini.3mf]
2020-05-04 Added MP10 0.4mm PLA 11X Earsaver
    Added PLA version of 11x earsaver 12x strap lock print.
    [PLA_04_11XEarSaver_MP10.3mf]
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2020-05-14 USCSW Mask V3
    [USCSW-Filtered_Mask-v3L.stl, USCSW-Filtered_Mask-v3M.stl, USCSW-Filtered_Mask-v3S.stl, USCSW-Filtrated_Mask-v2L.stl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]
2020-05-14 Printfarm added initial PLA Mask v3 print files to test
    Added initial test files of mask prints. Overhangs and breaking off the build plates have been issues.
    Added temperature towers to dial in PLA temps
    [PLA_04_1X_USCSW-v3L_MP10mini.3mf, PLA_04_1X_mask-v3L_MP10.3mf, PLA_04_2X_USCSW-v3L_MP10mini.3mf, PLA_04_TempTower_MP10mini_260-200.3mf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]
2020-05-16 Printfarm structure changes and added mask files
    - Printfarm folder changes to move all Cura project files into separate folders for cleaner organization
    - Added mask files for all current printfarm variants.
    - Added manual leveling procedure information to readme and updated files.
    [MP10_shieldV5_r041620_PLA.3mf, PETG_04_11XEarSaver_MP10.3mf, PETG_04_1XshieldV5_MP10.3mf, PETG_04_2XshieldV5_MP10.3mf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]
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2020-05-16 Added 2X Mask MP10 print files
    Added 2X Mask MP10 print files for 0.4 and 0.6 nozzles. Additional optimizations and model positioning in the slices
    [PLA_04_1X_mask-v3L_MP10.3mf, PLA_04_2X_mask-v3L_MP10.3mf, PLA_04_4X_mask-v3L_MP10.3mf, PLA_06_2X_mask-v3L_MP10.3mf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]
2020-05-16 Update mask print MP10 files
    Profile import lost some settings in previous operation. Resliced with latest changes.
    [PLA_04_1X_mask-v3L_MP10mini.3mf, PLA_04_2X_mask-v3L_MP10mini.3mf]
2020-05-16 Update 0.6 MP10 Mask Files
    Removed testing project files. Resliced after results for flow on front cap
    [PLA_06_1X_mask-v3L_MP10.3mf, PLA_06_2X_mask-v3L_MP10.3mf, PLA_06_4X_mask-v3L_MP10.3mf, con_PLA_06_1X_mask-v3L_MP10.3mf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]
2020-05-20 Printfarm: Reduce Mask print times on MP10 Mini
    Increase speed, temp, and flow on MP10 mini mask print files. Reduces each mask by approx 45minutes without reducing quality. Added strap locks to 1x mask print.
    [PLA_04_1X_mask-v3L_MP10mini.3mf, PLA_04_2X_mask-v3L_MP10mini.3mf]
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2020-06-07 Added Verkstan slices for 0.4mm nozzles
    First addition of Verkstan slices for the 0.4mm nozzle printfarm MP10 and Mini printers.
    Tested stack, but had poor results. Single prints only
    [PLA_04_1X_Verkstan_MP10mini.3mf, PLA_04_2X_Verkstan_MP10.3mf]
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2020-06-15 Updated body camera clip models
    New model version with widen arm portion for tighter clip.
    [PLA_04_12X_CamClip_MP10.3mf, PLA_04_6X_CamClip_MP10.3mf, PLA_04_6X_CamClip_MP10mini.3mf, PLA_04_8X_CamClip_MP10mini.3mf]
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
